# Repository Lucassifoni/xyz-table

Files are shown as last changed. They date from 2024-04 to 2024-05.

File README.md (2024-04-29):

# Low-BOM printable XYZ platform for Bath Interferometers

 Licensed under Creative Commons BY-NC-SA 4.0 

| | |
|-|-|
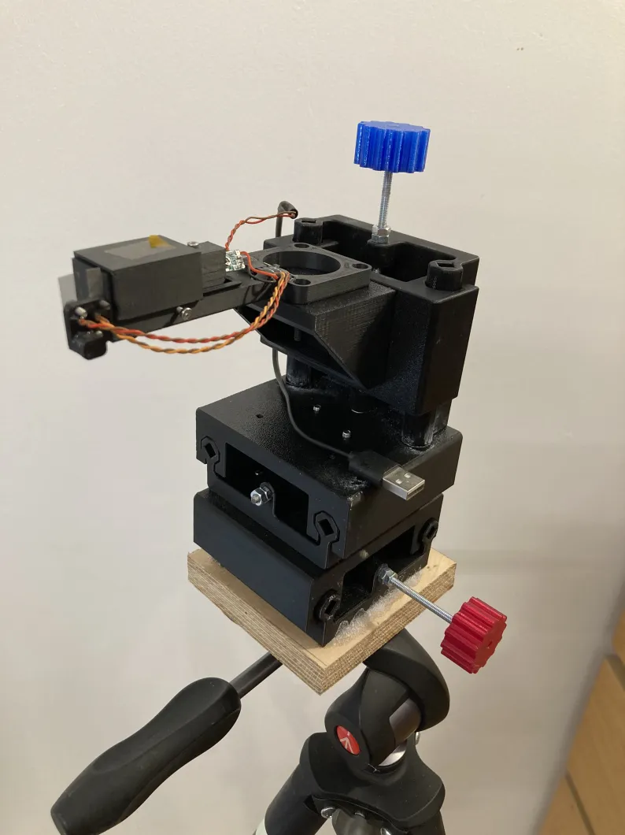
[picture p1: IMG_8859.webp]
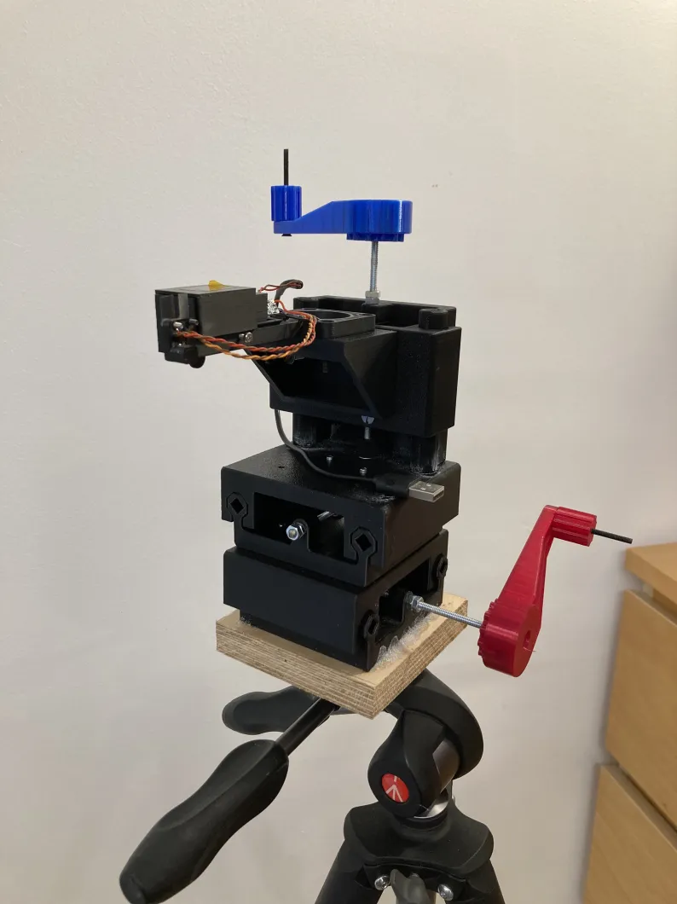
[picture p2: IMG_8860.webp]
| | |
| coarse controls | fine control handles |

## Please know your printer and use the TOLERANCE TEST

You have to print **everything** flawlessly for smooth motion. To determine what STLs to use, please print the TOLERANCE TEST. It should slide freely, with a bit of sanding if you mis-placed the seam while slicing.
**Pay attention to the seam position !** Seam traps are on the roadmap but not implemented yet.

### Why is the tolerance test so big ?

Good question : I found that my smaller tolerance tests (one rail only) did not give correct information as whether a whole stage would be smooth.

The tolerance is the fine space in this screenshot. The smallest you can print, the best :
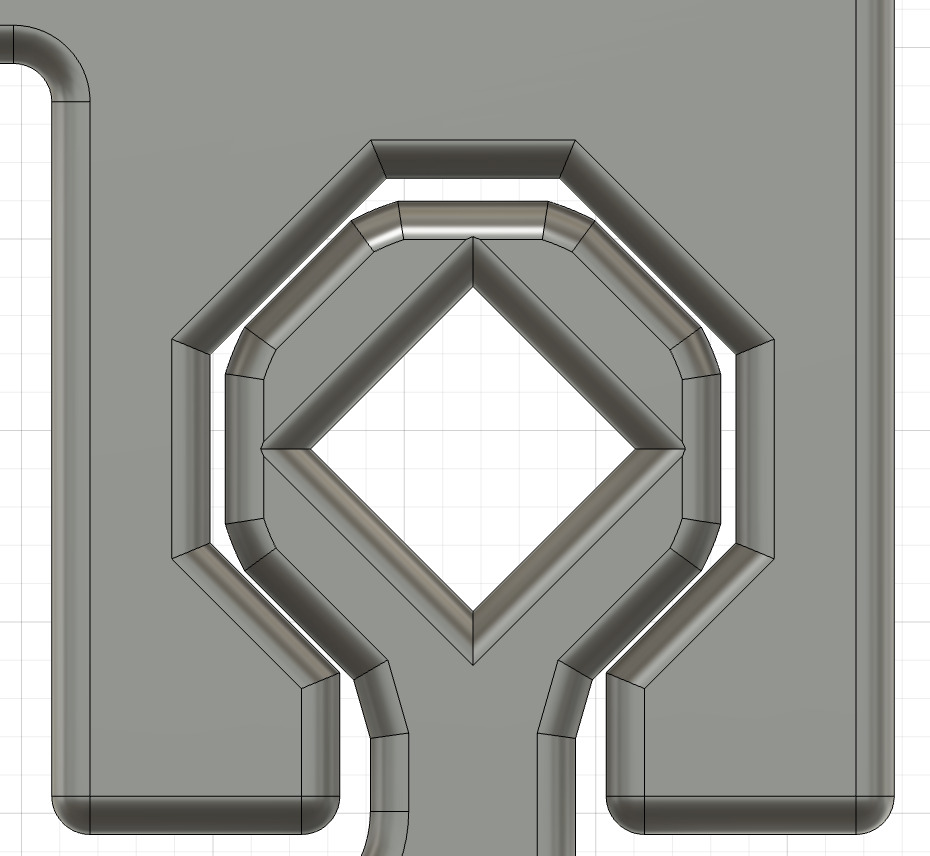
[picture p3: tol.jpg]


| Name | Value | Printed and tested |
|---|---|---|
| Tightest | 0.07mm |  ✅ (Bambu P1S) |
| Tight | 0.1mm |  |
| Easy | 0.125mm |  |

## Prints BOM

- Print the TOLERANCE TEST and choose accordingly
- Print everything in the `Common` folder in the quantities listed in file names
- Print everything in the folder corresponding to your chosen tolerance

## Vitamins BOM

| Design. | Quantity |
|-------|-------|
| M4 rod | 3 |
| M4 nut | 12 |
| M4 screw x 14mm | 16 |
| Superglue | Some |

Only uses M4 rods and M4 screws as vitamins. Superglue is used to lock the nuts and suppress Z axis wobble at the joint with the Y axis.

## A few tips :

- Dry your filament.
- Do not print too fast.
- Use PETG
- Re-tap the screw holes before assembly
- Tap the carrier blocks **with oil** before assembly

Thanks Paul for design advice !

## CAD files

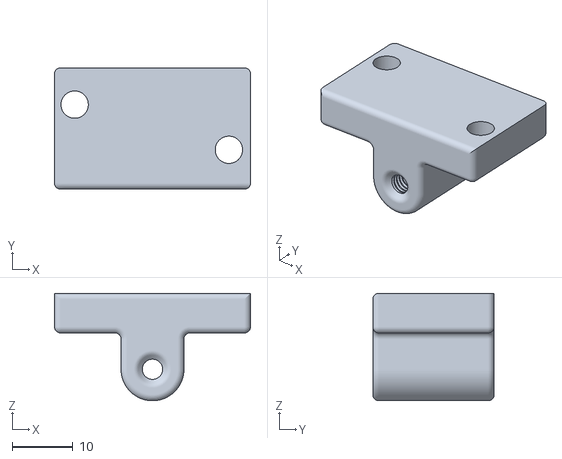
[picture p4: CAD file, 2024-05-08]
Common/Carrier_Block_x3.stl
32.3 x 20.0 x 17.7

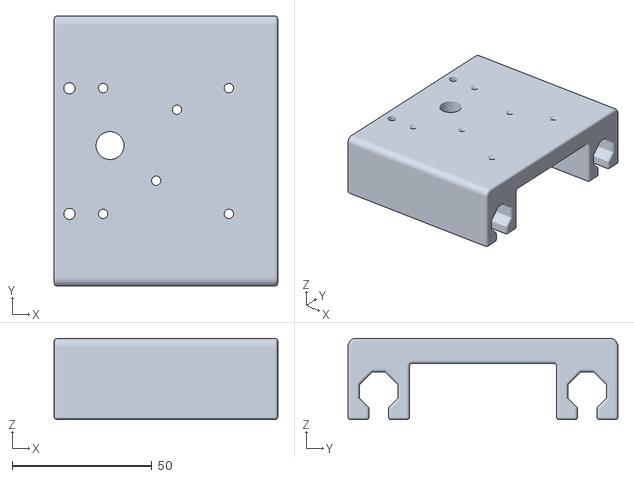
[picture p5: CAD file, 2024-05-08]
Easy/Y_Stage_High.stl
80.0 x 96.6 x 29.1

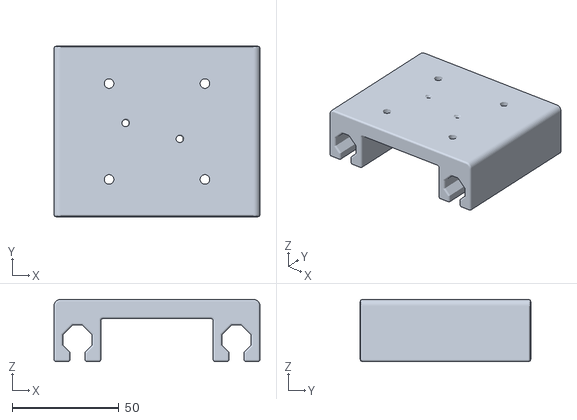
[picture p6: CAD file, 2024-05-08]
Tightest/X_Stage_High.stl
96.6 x 80.0 x 29.1

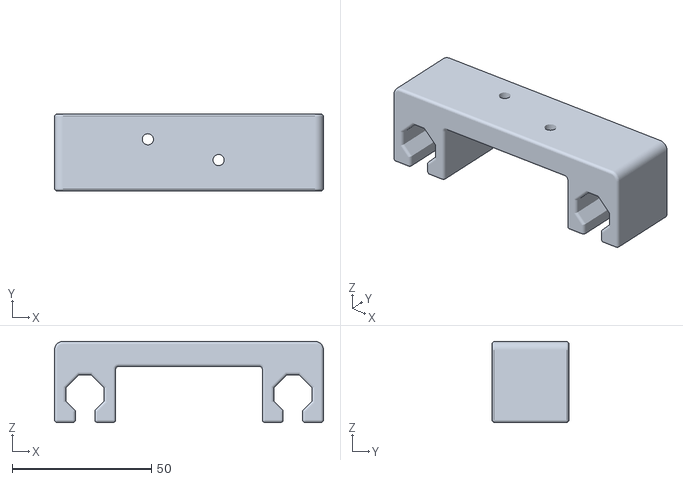
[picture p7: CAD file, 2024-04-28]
TOLERANCE TEST/Tolerance_Test_Tightest_High.stl
96.6 x 27.7 x 29.1

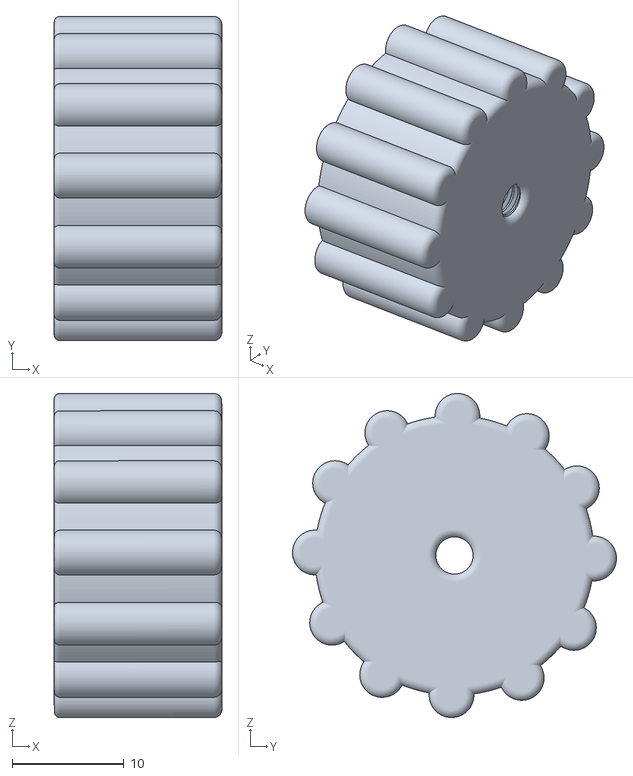
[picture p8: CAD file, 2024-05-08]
Common/Big_Knob_x3.stl
15.0 x 29.0 x 29.0

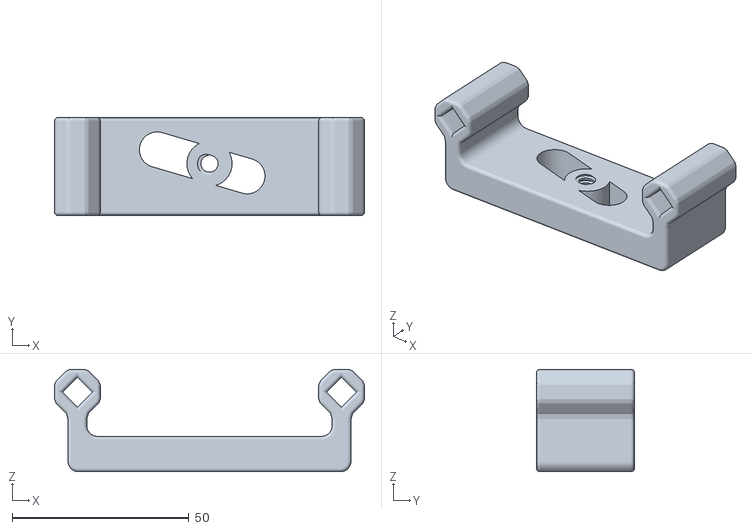
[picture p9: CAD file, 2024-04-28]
TOLERANCE TEST/Tolerance_Test_Easy_Low.stl
87.6 x 27.7 x 28.9

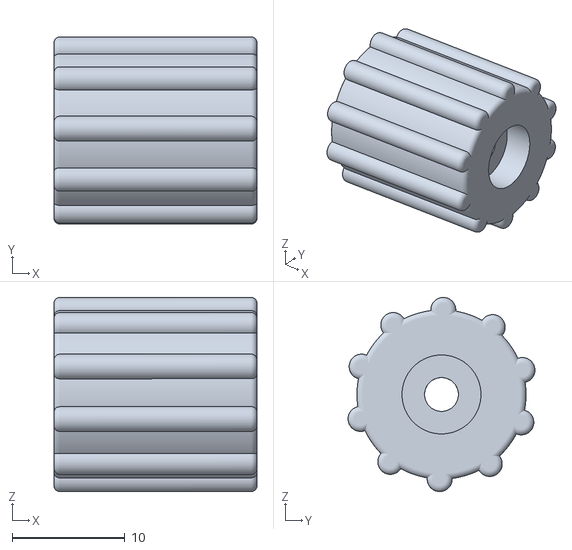
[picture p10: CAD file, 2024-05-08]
Common/Small_Knob_x3.stl
18.0 x 16.6 x 17.2

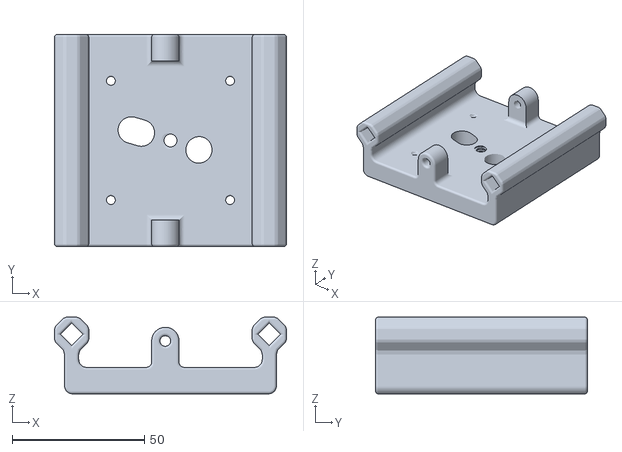
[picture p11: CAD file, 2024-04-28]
Easy/X_Stage_Low.stl
87.6 x 80.0 x 28.9

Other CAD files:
Red_5h58.gcode.3mf
Tight/Y_Stage_High.stl
Blue_6h23.gcode.3mf
Easy/X_Stage_High.stl
Tight/X_Stage_High.stl
Tightest/Y_Stage_High.stl
Green_6h.gcode.3mf
Tight/X_Stage_Low.stl
Tightest/X_Stage_Low.stl
TOLERANCE TEST/Tolerance_Test_Tight_High.stl
Common/Handle_x3.stl
Common/Interferometer_Carrier.stl
Easy/Y_Stage_Low.stl
Easy/Z_Stage_A.stl
Easy/Z_Stage_B.stl
TOLERANCE TEST/Tolerance_Test_Easy_High.stl
Tight/Y_Stage_Low.stl
Tight/Z_Stage_A.stl
Tight/Z_Stage_B.stl
Tightest/Y_Stage_Low.stl
Tightest/Z_Stage_A.stl
Tightest/Z_Stage_B.stl

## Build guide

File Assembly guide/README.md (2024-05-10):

# Assembly instructions

## Initial setup

| Instruction | Picture |
| -----------------|----------------|
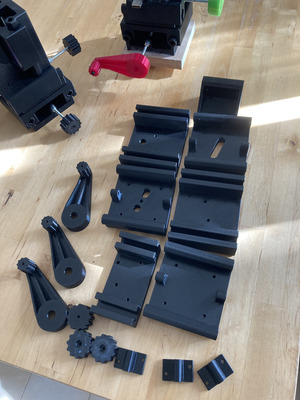
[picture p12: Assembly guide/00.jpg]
| - Gather pieces |  |
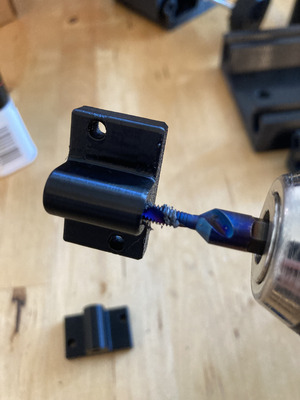
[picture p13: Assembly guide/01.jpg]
| - Tap the three carrier blocks with an M4 tap |  | 
| - Tap the Z interferometer carrier mounting holes with an M4 tap |  | 
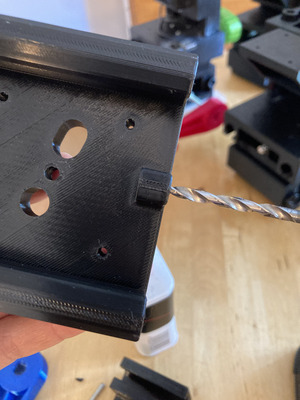
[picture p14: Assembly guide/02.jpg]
| - Cleanup the M4 rod guiding holes |  | 
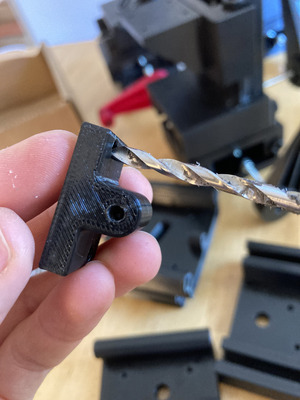
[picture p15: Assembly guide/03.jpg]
| - Cleanup the Carrier blocks mounting holes |  | 

## Z AXIS

| Instruction | Picture |
| -----------------|----------------|
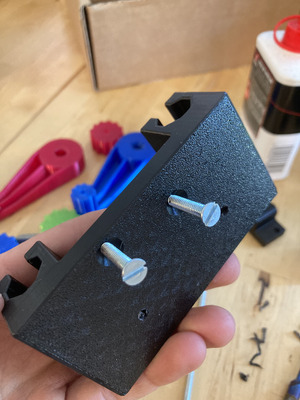
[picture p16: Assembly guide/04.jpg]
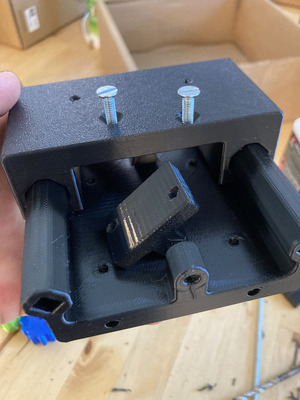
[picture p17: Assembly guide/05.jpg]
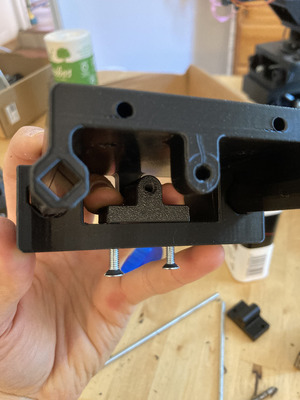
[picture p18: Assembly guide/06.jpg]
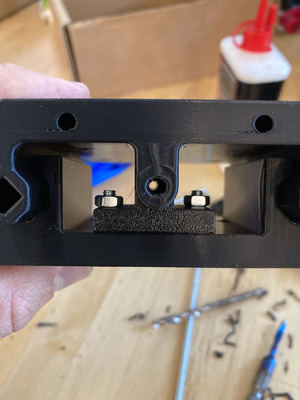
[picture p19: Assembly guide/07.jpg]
| - Mount the Z carrier block with two M4 flat head screws and nuts : pay attention to the orientation ! |     |
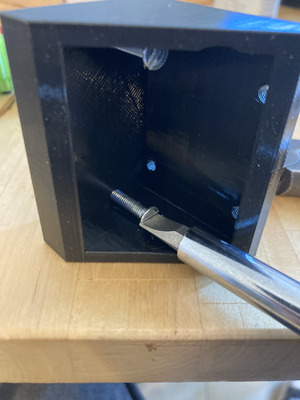
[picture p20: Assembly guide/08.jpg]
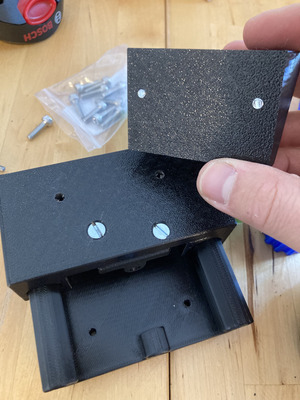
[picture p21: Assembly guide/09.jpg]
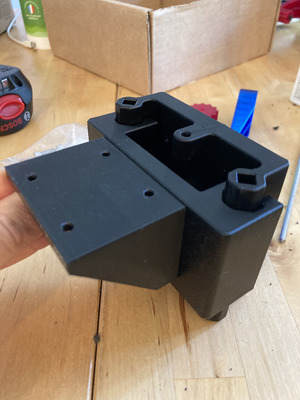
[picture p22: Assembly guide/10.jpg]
| - Mount the interferometer carrier |    |
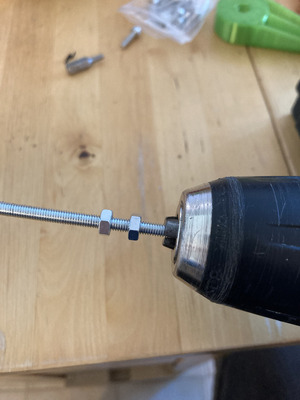
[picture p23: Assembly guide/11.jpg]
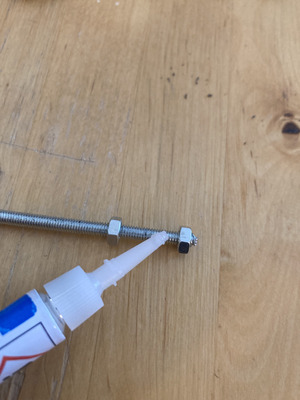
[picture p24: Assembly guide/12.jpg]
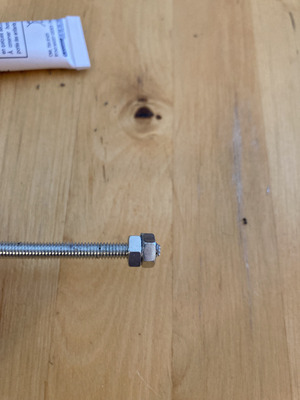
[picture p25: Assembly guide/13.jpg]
| - Prepare a M4 rod with two M4 nuts tightened against each other at the end and secured with cyanoacrylate glue |     |
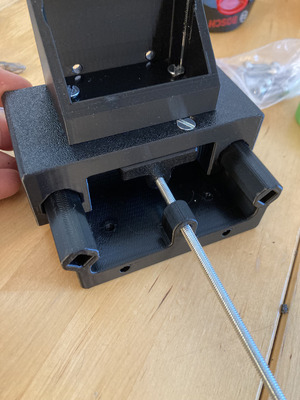
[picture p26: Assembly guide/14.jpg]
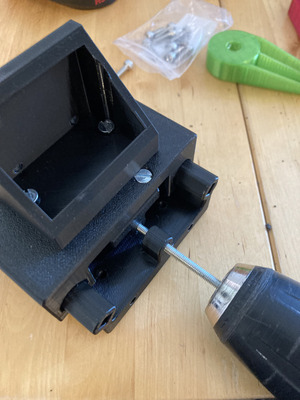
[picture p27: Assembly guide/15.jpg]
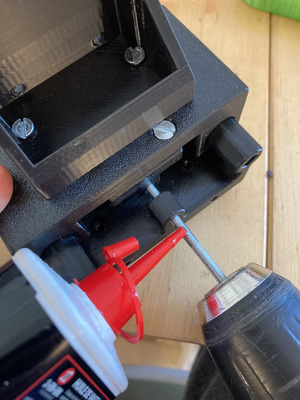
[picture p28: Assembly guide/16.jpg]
| - This becomes a kind of handle : use it to run the rod through the whole Z stage, starting at the bottom |    |
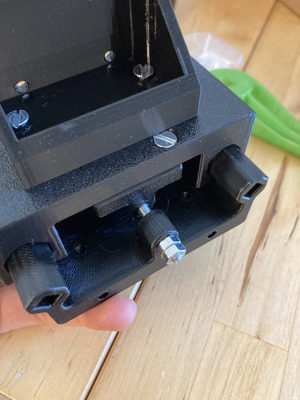
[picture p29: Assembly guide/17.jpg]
| - Butt the two nuts against the lower Z rod guide |  |
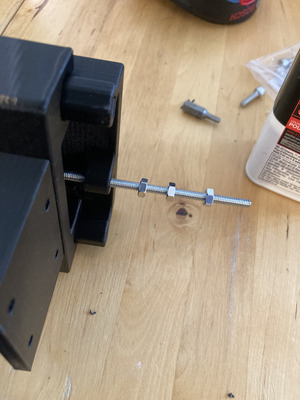
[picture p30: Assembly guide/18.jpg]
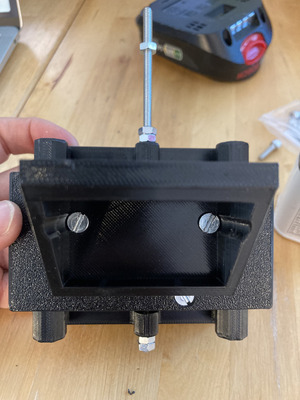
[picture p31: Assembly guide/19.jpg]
| - On the other side, run three nuts, two of which must butt against the upper Z rod guide, be tightened against each other, and secured with CA glue. They must butt against the guide as any space left here will become backlash in the Z axis. |   |
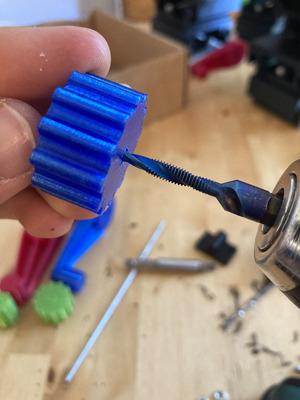
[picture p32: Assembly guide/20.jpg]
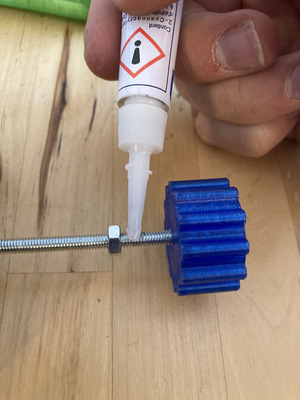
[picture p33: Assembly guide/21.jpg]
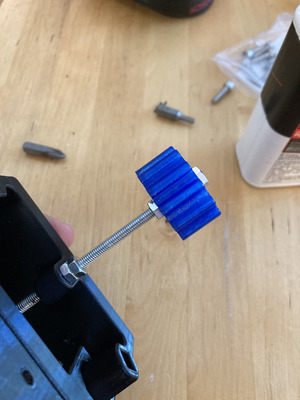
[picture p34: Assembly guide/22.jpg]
| - Add the Z knob, add another M4 nut, and secure this assembly very well by tightening it and adding CA glue |    |
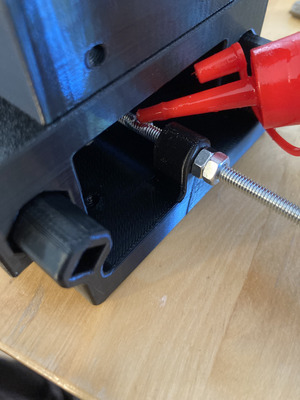
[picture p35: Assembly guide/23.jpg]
| - Add oil on the rod, on both sides of the Z carrier block, and where the nuts butt against the guides. |  |
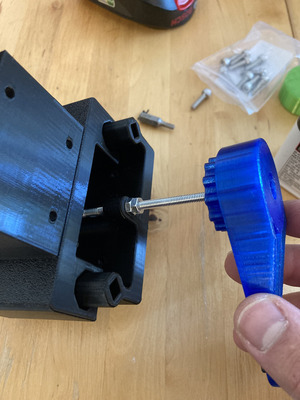
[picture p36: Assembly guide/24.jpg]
| - Add the Z handle  |  |

**Congratulations ! You have completed the Z axis !**

## Y AXIS

| Instruction | Picture |
| -----------------|----------------|
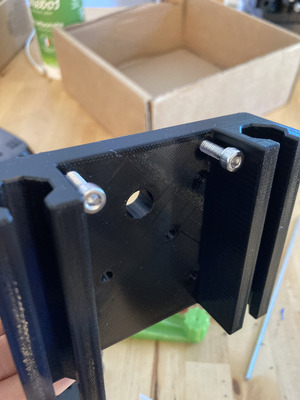
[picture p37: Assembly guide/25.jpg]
| - Take the Y axis upper part and run 2 M4 screws through the Z axis mounting holes |   | 
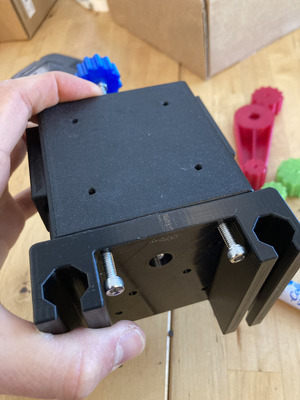
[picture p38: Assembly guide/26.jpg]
| - Screw the Z axis to the Y axis |   | 
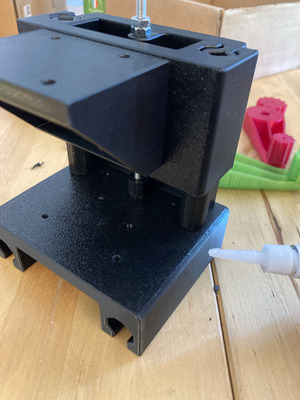
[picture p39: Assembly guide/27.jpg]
| - Add CA glue where the two Z axis pillars meet the Y axis top |  | 
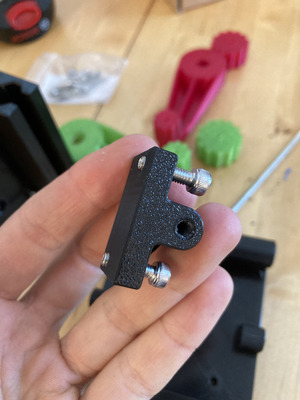
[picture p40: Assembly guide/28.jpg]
| - Take the Y axis carrier block and run two M4 screws through it |  | 
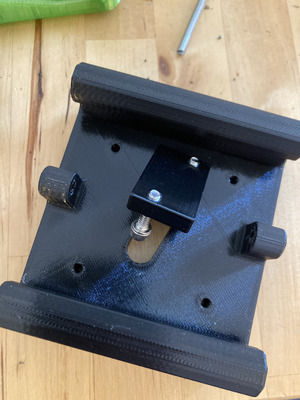
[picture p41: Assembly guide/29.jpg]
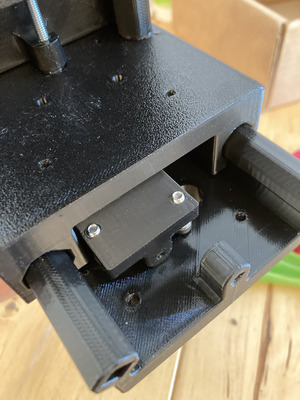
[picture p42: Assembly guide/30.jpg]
| - Place it on the lower Y axis, and run this in the Y gliders |     | 
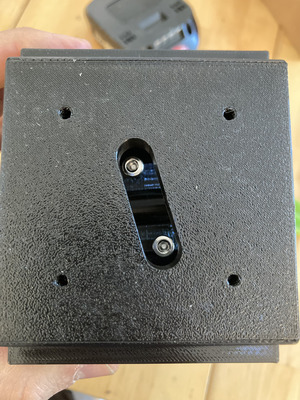
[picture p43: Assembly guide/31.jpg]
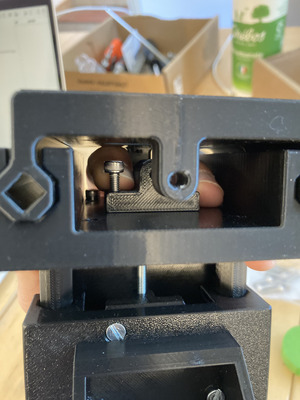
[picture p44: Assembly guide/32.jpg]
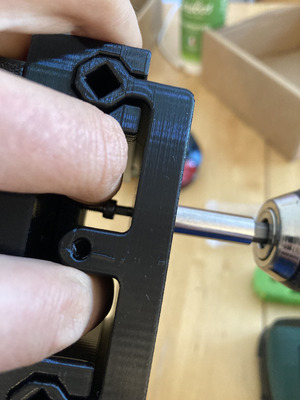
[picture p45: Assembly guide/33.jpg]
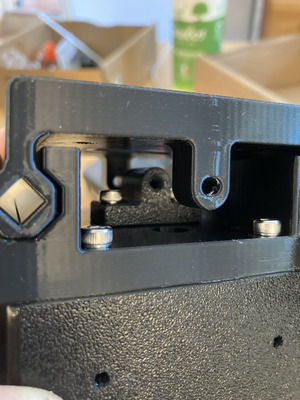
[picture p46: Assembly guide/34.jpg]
| - Flip the assembly and secure the screws through the hole |    | 
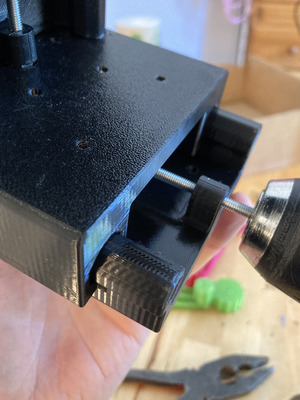
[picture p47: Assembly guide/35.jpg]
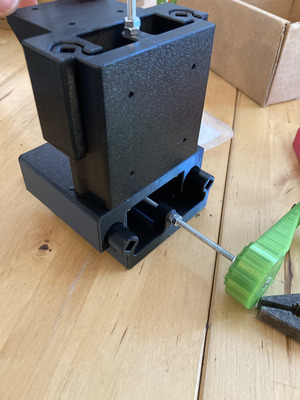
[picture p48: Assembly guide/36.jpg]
| - You now have a free-gliding Y axis. Repeat the steps of the Z rod assembly to add motion. |   | 

**Congratulations ! You have completed the Y axis !**

## X AXIS

| Instruction | Picture |
| -----------------|----------------|
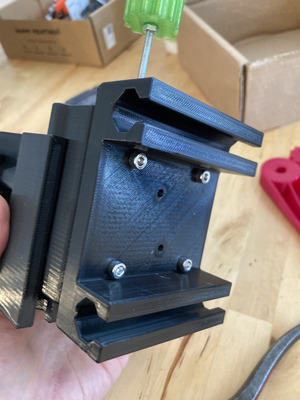
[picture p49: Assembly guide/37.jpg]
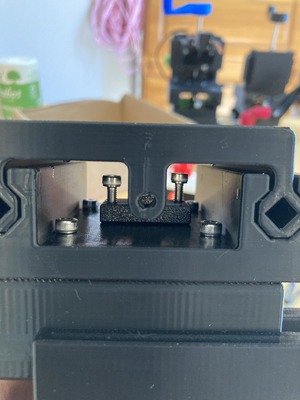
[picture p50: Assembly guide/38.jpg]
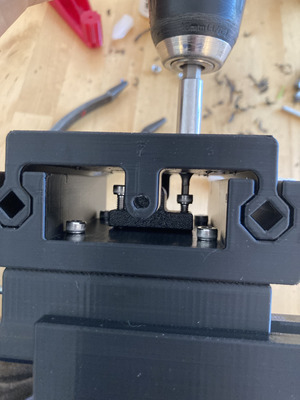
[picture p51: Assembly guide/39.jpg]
| - Repeat those same steps for the X axis. |    | 

**Congratulations ! You have a full XYZ table !**



## BEFORE USE

- Lubricate every mating surface on every axis
- Lubricate every spot where nuts butt against rod guides
- Lubricate rods on each side of the carrier blocks
- Run each axis two times from an end to another

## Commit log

2024-04-28 Adds various tolerances
    [All_handles.3mf, Big_Knob_x3.stl, Carrier_Block.stl, Carrier_Block_x3.stl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]
2024-04-28 Fixes model
    [X_Stage_Low.stl]
2024-05-08 Regens files with comfort changes
    [Big_Knob_x3.stl, Carrier_Block_x3.stl, Interferometer_Carrier.stl, Small_Knob_x3.stl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]
2024-05-10 Adds assembly guide
2024-06-21 Adds pre-seamed 3MF files
    [Blue_6h23.gcode.3mf, Green_6h.gcode.3mf, Red_5h58.gcode.3mf]
